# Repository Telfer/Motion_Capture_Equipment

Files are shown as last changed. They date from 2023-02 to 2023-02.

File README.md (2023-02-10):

# Motion_Capture_Equipment
 Just some bits and bobs that were developed while working in and around motion capture labs for the past few years

## Marker skeleton

Mesh files: marker_holder.stl

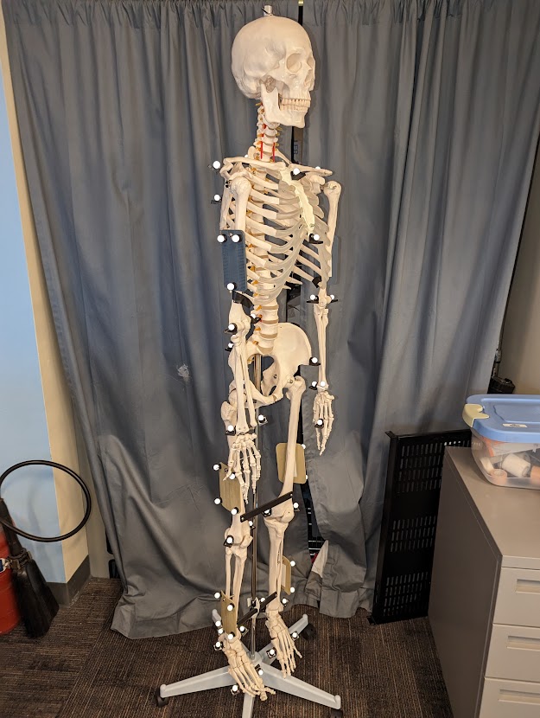
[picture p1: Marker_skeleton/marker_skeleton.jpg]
Marker skeleton


After forgeting to put a marker on for the n-th time, I bought a cheap anatomical skeleton, printed these little marker holders, and started using this set up as a way both to store the markers (pre-taped) and show the landmarks where they need to go. We just put the skeleton next to the participant and transfer the markers over one at a time. Usually easy to see if one has been missed. If you use multiple marker sets you could potentially color code or something. 

Designed for ~18mm (3/4 inch) tape. I used short (~12mm) M3 or M4 screws to attach the marker holders to the bones, along with longer ones to hang the marker plates from. Depending on your skeleton, you may also need to make extra plates to attach between bones and stop it swinging around.

## Marker plates

Mesh files: marker_plate_120-72-11.stl, marker_plate_120-80-9.stl, and marker_plate_120-60-6.stl

These do the job and are a lot less expensive than the ones I've seen commericially. The stl files are the plates I use for shank, thigh, and upper arm. These seem to work well but can be easily scaled to generate custom sizes. Be sure to print flat on the build plate for optimal strength. Both PETG and PLA have worked for me. I just superglue markers to each corner.

## Hindfoot wand

Mesh files: HeelPlate.stl, MarkerPlate.stl

Two-part marker plate designed to allow a shoe with a heel window cut in it to be taken on and off during a motion capture study (for example on different types of foot orthoses). Instructions on use in the pdf. Used in [Dose response effects of FOs](https://pubmed.ncbi.nlm.nih.gov/23631857/) and a few other papers.

## Markers with radio-opaque centers

Mesh files: Marker_RO_center_bottom.stl, Marker_RO_center_top.stl

We use these for biplane fluoroscopy studies that also require optical motion capture measurements. The marker is printed in 2 parts, a steel ball bearing is placed in the center and the 2 halves glued together. Finally, cover the marker in reflective 3M tape and you have a marker that can be measured using both biplane and standard motion capture systems. I've included stl files for a sample 9mm marker with for 3mm diameter center bead (we use these for feet), but there is also a quick python script for Rhino to generate custom markers with different hole and overall sizes.

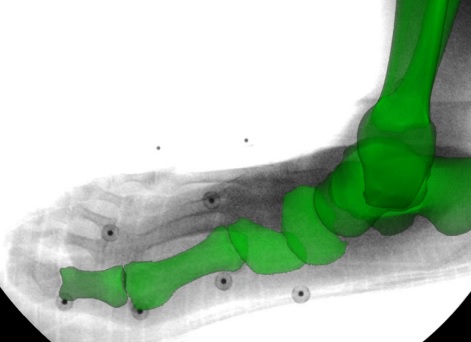
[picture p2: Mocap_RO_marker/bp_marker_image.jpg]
Marker under fluoroscopy


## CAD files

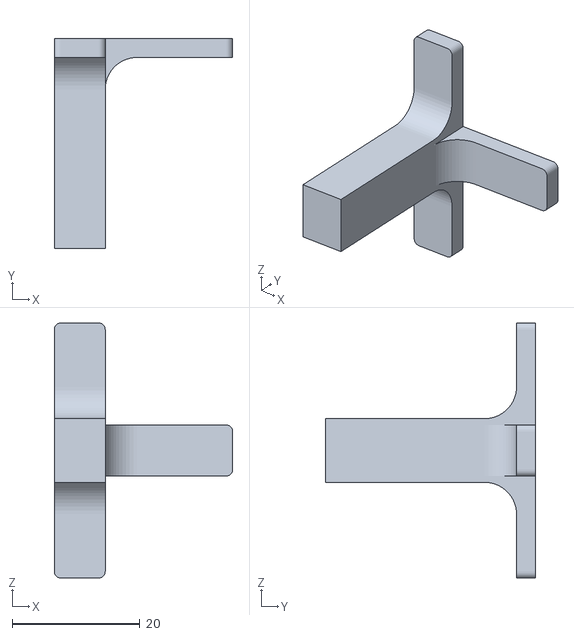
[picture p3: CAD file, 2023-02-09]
Hindfoot_wand/MarkerPlate.stl
28.0 x 33.0 x 40.0

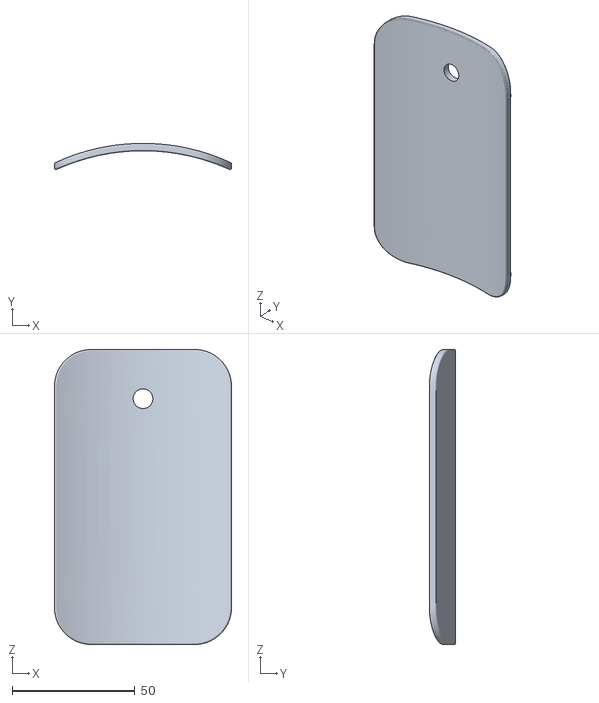
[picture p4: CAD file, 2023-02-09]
Marker_plates/marker_plate_120-72-11.stl
72.0 x 10.7 x 120.0

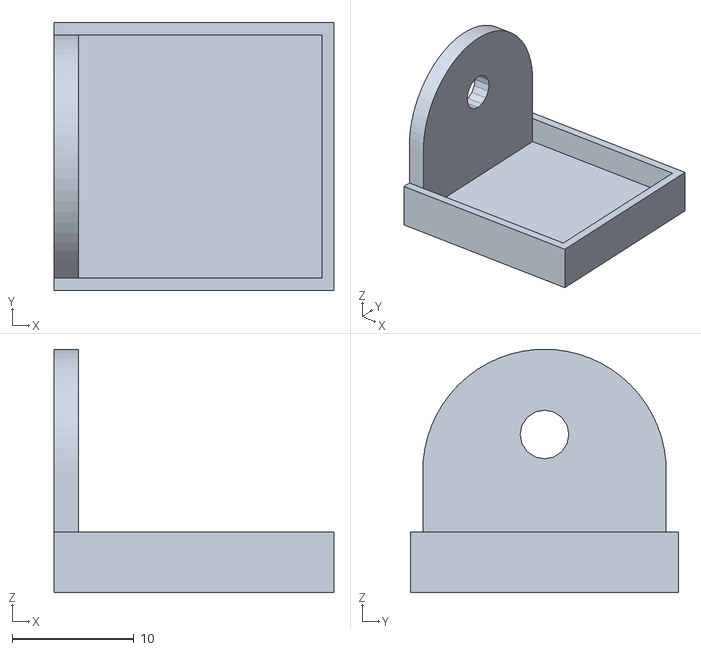
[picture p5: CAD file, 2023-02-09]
Marker_skeleton/marker_holder.stl
23.0 x 22.0 x 20.0

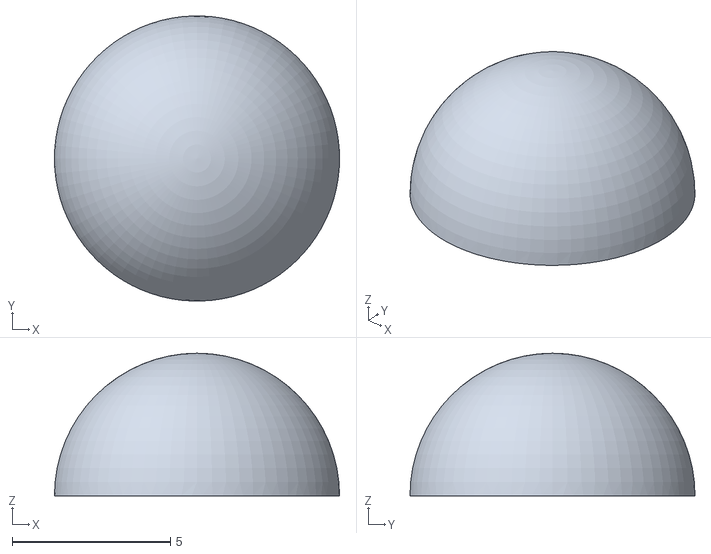
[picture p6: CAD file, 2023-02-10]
Mocap_RO_marker/Marker_RO_center_top.stl
9.00 x 8.99 x 4.50

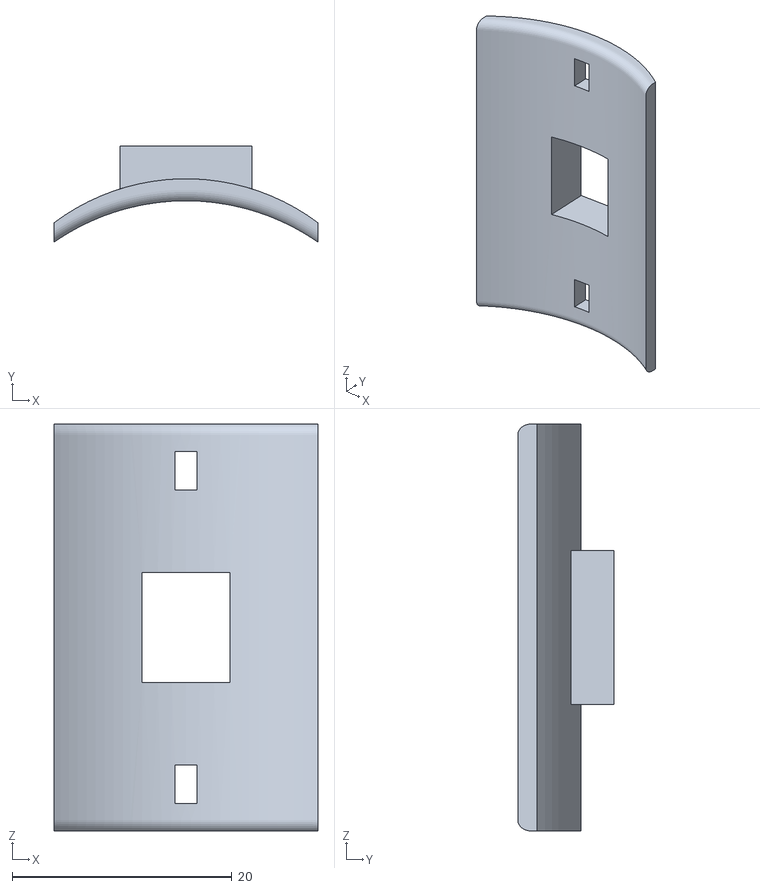
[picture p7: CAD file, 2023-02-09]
Hindfoot_wand/HeelPlate.stl
24.0 x 8.77 x 37.0

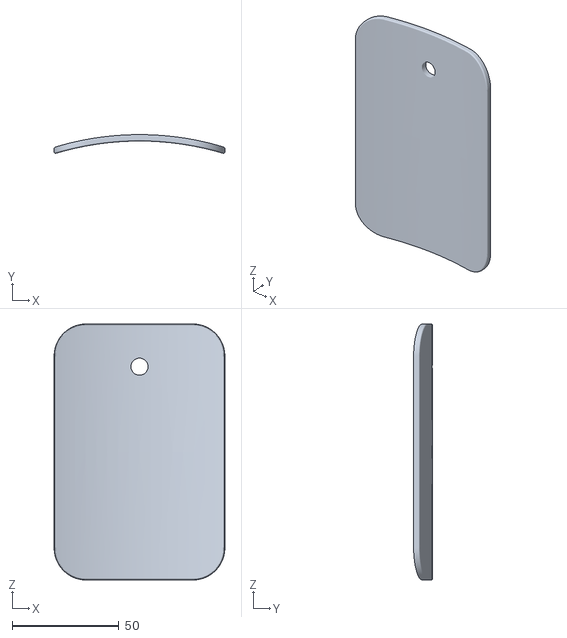
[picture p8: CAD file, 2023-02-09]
Marker_plates/marker_plate_120-80-9.stl
80.0 x 8.79 x 120.0

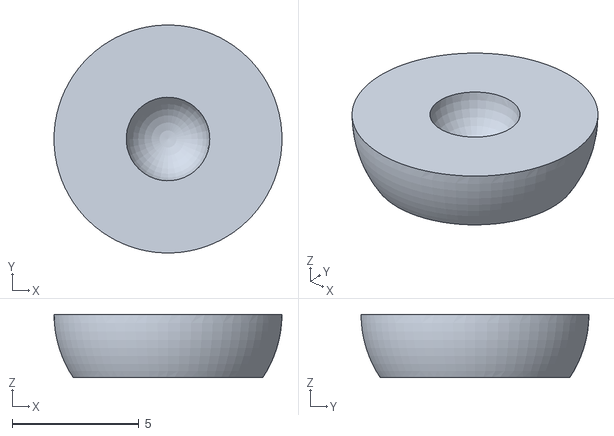
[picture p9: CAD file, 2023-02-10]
Mocap_RO_marker/Marker_RO_center_bottom.stl
9.00 x 8.99 x 2.50

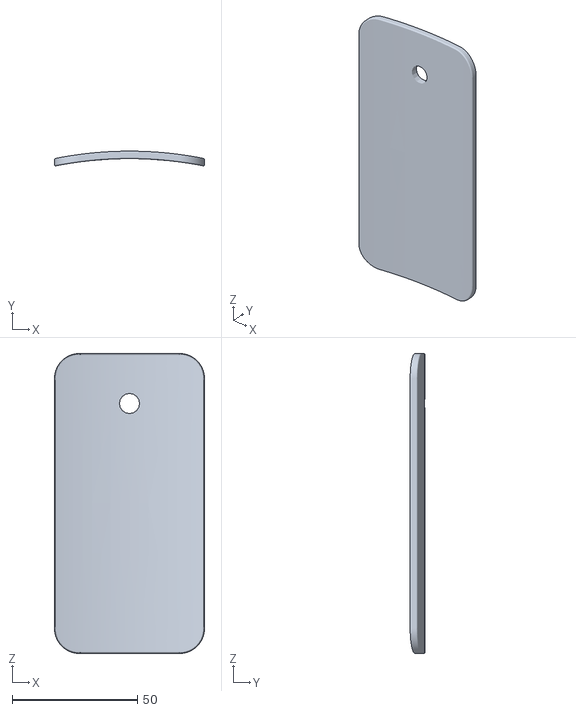
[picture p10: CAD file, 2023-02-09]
Marker_plates/marker_plate_120-60-6.stl
60.0 x 5.89 x 120.0

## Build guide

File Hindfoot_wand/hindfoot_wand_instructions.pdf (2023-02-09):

2

## Dose-response effects of customised foot orthoses on lower limb kinematics and kinetics in pronated foot type: supplementary materials

Telfer S*, Abbott M, Steultjens M, Woodburn J

All authors: School of Health and Life Sciences, Glasgow Caledonian University, UK

*Corresponding author

Address: Institute of Applied Health Research, Glasgow Caledonian University, Cowcaddens Road, Glasgow, UK, G4 0BA

Telephone: +44 (0) 141 331 8475

Email: scott.telfer@gcu.ac.uk

3

## Contents

4

## 1. Motion capture model

### 1.1 Marker locations

All retroreflective motion capture markers were flat-based spherical type (Qualysis AB, Gothenburg, Sweden). Marker locations and details are described in Table S1 and Figure S1.

Table S1 –Marker locations, labels and function
Number | Landmark/Location | Label Name | Size (mm) | Remove*/Track
1 | Right anterior iliac spine | RAIS | 19 | Tracking
2 | Right greater trochanter | RGT | 19 | Remove
3 | Right posterior iliac spine | RPIS | 19 | Tracking
4 | Left anterior iliac spine | LAIS | 19 | Tracking
5 | Left greater trochanter | LGT | 19 | Remove
6 | Left posterior iliac spine | LPIS | 19 | Tracking
7 | Thigh 1st | THI1 | 19 | Tracking
8 | Thigh 2nd | THI2 | 19 | Tracking
9 | Thigh 3rd | THI3 | 19 | Tracking
10 | Thigh 4th | THI4 | 19 | Tracking
11 | Lateral epicondile | LKNE | 12 | Remove
12 | Medial epicondile | MKNE | 12 | Remove
13 | Shin 1st | SHN1 | 19 | Tracking
14 | Shin 2nd | SHN2 | 19 | Tracking
15 | Shin 3rd | SHN3 | 19 | Tracking
16 | Shin 4th | SHN4 | 19 | Tracking
17 | Medial malleolus | MMAL | 7 | Remove
18 | Lateral malleolus | LMAL | 7 | Remove
19 | Superior calcaneum | SCAL | 7 | Tracking
20 | Inferior calcaneum | ICAL | 7 | Tracking
21 | Lateral offset calcaneum | OCAL | 7 | Tracking
22 | Medial calcaneum | MCAL | 7 | Remove
23 | Tuberosity navicular | NAV | 12 | Tracking
24 | Proximal 1st met | P1MT | 7 | Remove
25 | Medial 1st met head | M1MH | 12 | Tracking
26 2
| nd Met Head | D2MT | 7 | Remove
27 | Lateral calcaneum | LCAL | 7 | Remove
28 | Proximal 5th met | P5TH | 12 | Tracking
29 | Distal 5th met | D5TH | 12 | Tracking
*Remove: Required for model building only, removed after static trial has been captured

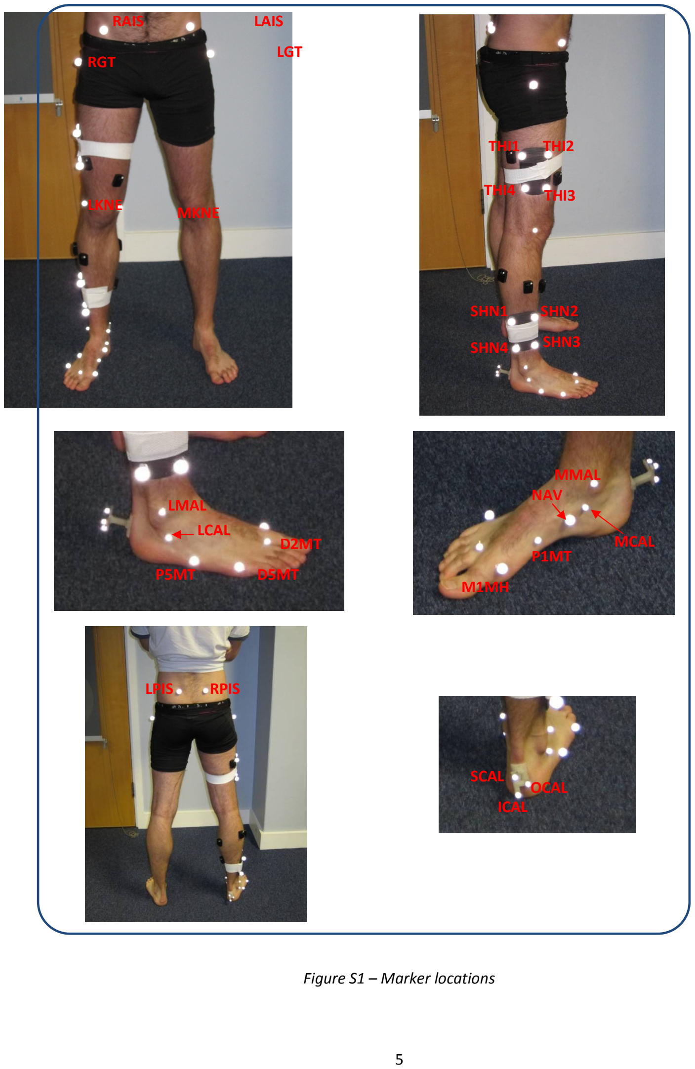
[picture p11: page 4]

5

Figure S1 – Marker locations

LGT

MKNE LKNE

RAIS | LAIS

RGT

THI1 THI2

THI3 THI4

SHN1 SHN2

SHN3 SHN4

MMAL

MCAL

NAV

P1MT

M1MH

SCAL

ICAL

OCAL

LPIS RPIS

D2MT

P5MT | D5MT

LCAL

LMAL

6

### 1.2 Anatomical reference frame definitions

Table S2 – Anatomical reference frame definitions for individual segments
Segment | Description
Pelvis | CODA¹
Thigh
Origin | Virtual HIP_CENTRE marker from CODA pelvis
z-axis | The z-axis is the projection of the line joining HIP_CENTRE and the origin.
x-axis | The x-axis is perpendicular to the z-axis in a plane containing the origin, KNEE, and LKNEE.
y-axis | The y-axis is mutually perpendicular to the x- and z-axes
Shank
Origin | A virtual KNEE marker was created 50% of the distance on the line between the LKNEE and MKNEE
| markers.
z-axis | A virtual marker, MAL_CENTRE is created 50% of the distance between the MMAL and LMAL markers.
| The z-axis is the projection of the line joining MAL_CENTRE and the origin.
x-axis | The x-axis is perpendicular to the z-axis in a plane containing the origin, MAL-centre and LMAL.
y-axis | The y-axis is mutually perpendicular to the x- and z-axes.
Rearfoot
Origin | A virtual marker is projected perpendicularly from SCAL onto a plane created by ICAL and virtual
| markers projected from ICAL in X + and Z + a nominal distance of 0.1m. The rearfoot origin is located
| here.
z-axis | The z-axis is the projection of the line joining ICAL and the rearfoot origin.
x-axis | The x-axis is perpendicular to the z axis in a plane containing the origin, ICAL and HF_X. HF_X is a
| virtual marker projected from the origin in the X + , a nominal distance of 0.1m.
y-axis | The y-axis is mutually perpendicular to the x- and z-axes.
Forefoot
Origin | Virtual markers are projected from P1MT (P1MT_PROJ) and P5MT (P5MT_PROJ) perpendicularly onto
| a plane created by D5MT and virtual markers projected from D5MT in X + and Y⁺ a nominal distance
| of 0.1m. The origin of the forefoot is then located at the midpoint (50% distance) between
| P1MT_PROJ and P5MT_PROJ.
y-axis | A virtual D2MT marker (D2MT_PROJ) is projected perpendicularly onto a plane created by D5MT and
| virtual markers projected from D5MT in X + and Y⁺ a nominal distance of 0.1m. The y-axis is a
| projection of the line joining the origin to D2MT_PROJ.
x-axis | The x-axis is perpendicular to the y-axis in a plane containing the origin, D2MT_PROJ and D5MT.
z-axis | The z-axis is mutually perpendicular to the y- and x-axes.
Foot
Origin | The origin is located at the virtual MAL_CENTRE marker.
y-axis | Virtual markers are created from projections in Y + from M1MH (M1MH_PROJ) and D5MT (D5MT_PROJ)
| to the longest toe. These distances are derived from calliper measurements for each subject. The y-
| axis is a projection of the line joining the origin and a virtual marker (DISTAL_FOOT_CENTRE) 50%
| distance between M1MH_PROJ and D5MT_PROJ.
z-axis | The z-axis is perpendicular to the y-axis in a plane containing the origin, DISTAL_FOOT_CENTRE and
| shank origin.
x-axis | The x-axis is mutually perpendicular to the y- and z-axes.

1

See http://www.c-motion.com/v3dwiki/index.php?title=Coda_Pelvis (last accessed 9th October 2012).

7

The landmarks outlined in Table S1, along with projected or virtual markers created within the Visual3D software system were used to define the segment anatomical reference frames (see Table S2). Orientation of the axes was standardised such that the X-axis was medial/lateral with X

+
pointing to the right; the Y-axis was anterior/posterior with Y

+
pointing forward; and the Z-axis as vertical with Z

+
pointing upwards.

### 1.3 Joint rotation definitions

The cardan sequence order of rotation was x-y-z. Intersegment rotations were defined using clinical meaningful terms. For the reported results, the knee joint kinetics were expressed in the local coordinate system of the thigh. Therefore external adduction (+) / abduction (-) moments occurred about the y-axis. Ankle joint kinetics were expressed in the local coordinate system of the shank. Therefore inversion (+) / eversion (-) occurred about the y-axis.

Rearfoot motion was expressed in the local coordinate system of the shank. Therefore inversion (+) / eversion (-) occurred about the y-axis. Motion of the tibia was expressed in the local coordinate system of the rearfoot. Therefore external (+) / internal (-) rotation was expressed about the z-axis. Forefoot motion was expressed in the local coordinate system of the rearfoot. Therefore adduction (+) / abduction (-) rotation occurred about the z-axis.

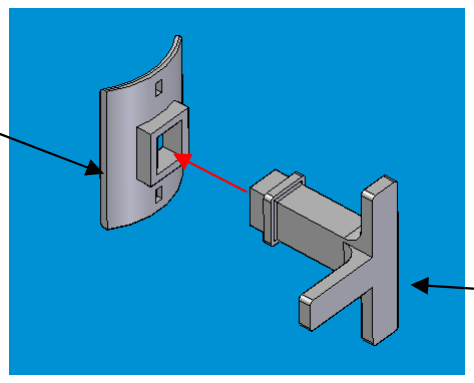
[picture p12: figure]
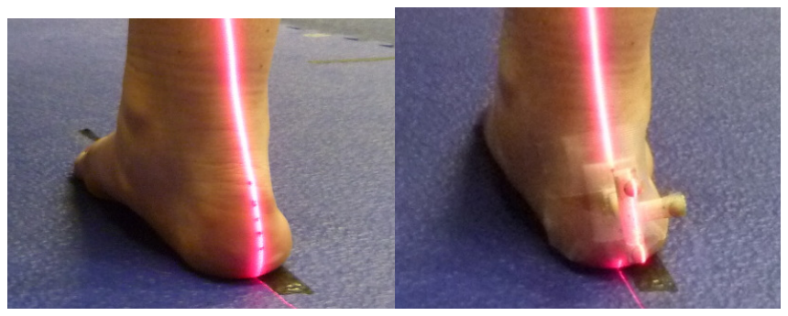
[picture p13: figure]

8

## 2. Footwear and accessories

### 2.1 Rearfoot wand

The rearfoot wand (Figure S2) is in two sections to allow a shoe to be donned and doffed without the need to fully remove and replace the wand, a process which would introduce error into the measurement. The wand is made up of a “plate” part, which is stuck to the participant’s heel, and the removable “wand” section which slots into a hole in the plate and has three markers stuck to it (SCAL, ICAL and OCAL). All parts were made in polyacidite via a fused deposition 3D printing method. The rearfoot wand and its CAD models are available on request from the corresponding author (scott.telfer@gcu.ac.uk).

Figure S2 – Detachable rearfoot wand

### 2.2 Positioning of rearfoot wand

Figure S3 – Alignment of rearfoot wand

To ensure accurate alignment of the rearfoot wand with the rearfoot in the frontal plane, the following protocol was used-

1. The calcaneal bisection line is drawn on the participant’s heel using a dark coloured nonpermanent marker.
2. The foot is positioned on the floor such that the 2nd toe and centre of the heel are aligned against a straight line marked on the floor while the participant stands in a relaxed position.
3. A line laser (red line laser, adjustable focus; A1 Technologies, London, UK) is positioned such that, when its line is vertical, it is aligned with the previously described line on the

WAND

PLATE

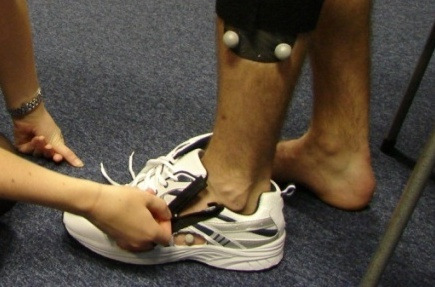
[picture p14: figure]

9

floor (see Figure S3). The laser is used to project a line onto the heel and lower leg. This laser is rotated until the projected line passes through the calcaneal bisection line previously marked on the heel (i.e. it matches the relaxed calcaneal stance position angle).

4. The rearfoot wand is then positioned so that laser line passes through the middle of both SCAL and ICAL markers (see figure S3).

### 2.3 Adapted shoe

A specially adapted neutrally posted training shoe was used in this study. The shoe has holes cut to allow the M1MH, P1MT, NAV and D5MT markers to be viewed as well as a hole in the heel counter to allow the rearfoot wand to stick through. Zips are sewn into the medial and lateral sides of the shoe to allow the upper to be opened up and the foot removed from the shoe without the need to remove and replace markers, while maintaining the structural integrity of the shoe.

As shown in Figure S4, to change the orthotic being worn, the detachable wand section of the rearfoot wand is carefully removed from the plate (leaving the plate attached to the foot) and the zips on the lateral and medial sides of the shoe are undone. The upper section opened out, and the researcher holds out the sides of the shoe. The participant is asked to push their toes as far as possible to the front of the shoe, then to first lift their heel out followed by the rest of the foot. This process is reversed to don the shoe.

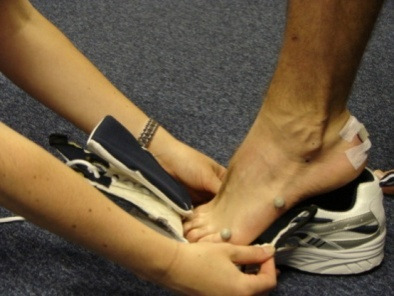
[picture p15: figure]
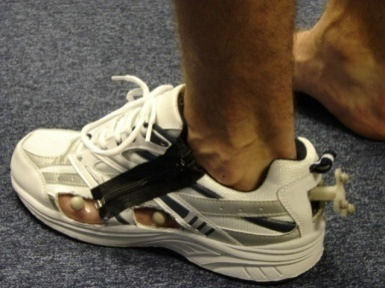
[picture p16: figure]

Figure S4 – Adapted shoe and process for changing orthotic

## 3. Additional results

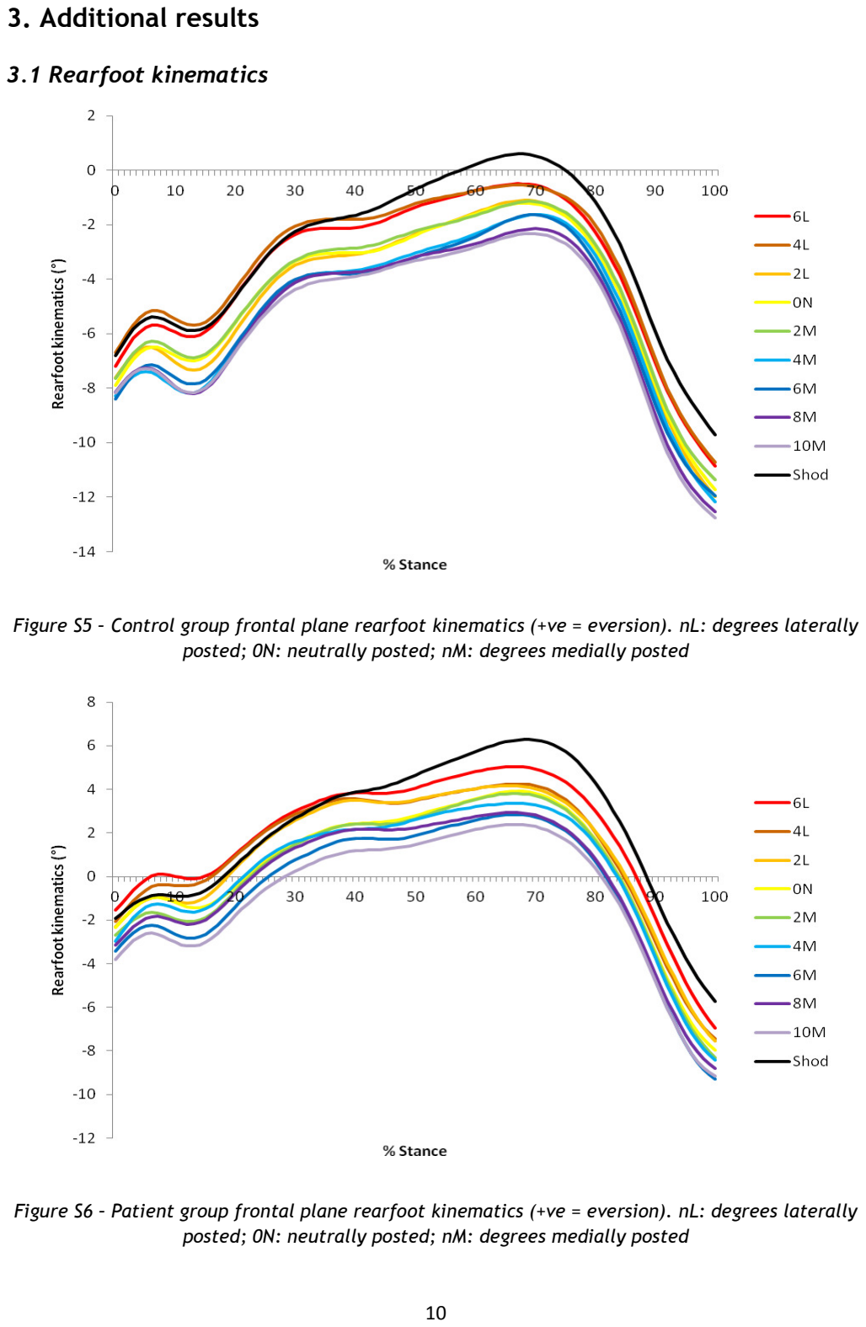
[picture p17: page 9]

10

### 3.1 Rearfoot kinematics

Figure S5 – Control group frontal plane rearfoot kinematics (+ve = eversion). nL: degrees laterally posted; 0N: neutrally posted; nM: degrees medially posted

Figure S6 – Patient group frontal plane rearfoot kinematics (+ve = eversion). nL: degrees laterally posted; 0N: neutrally posted; nM: degrees medially posted

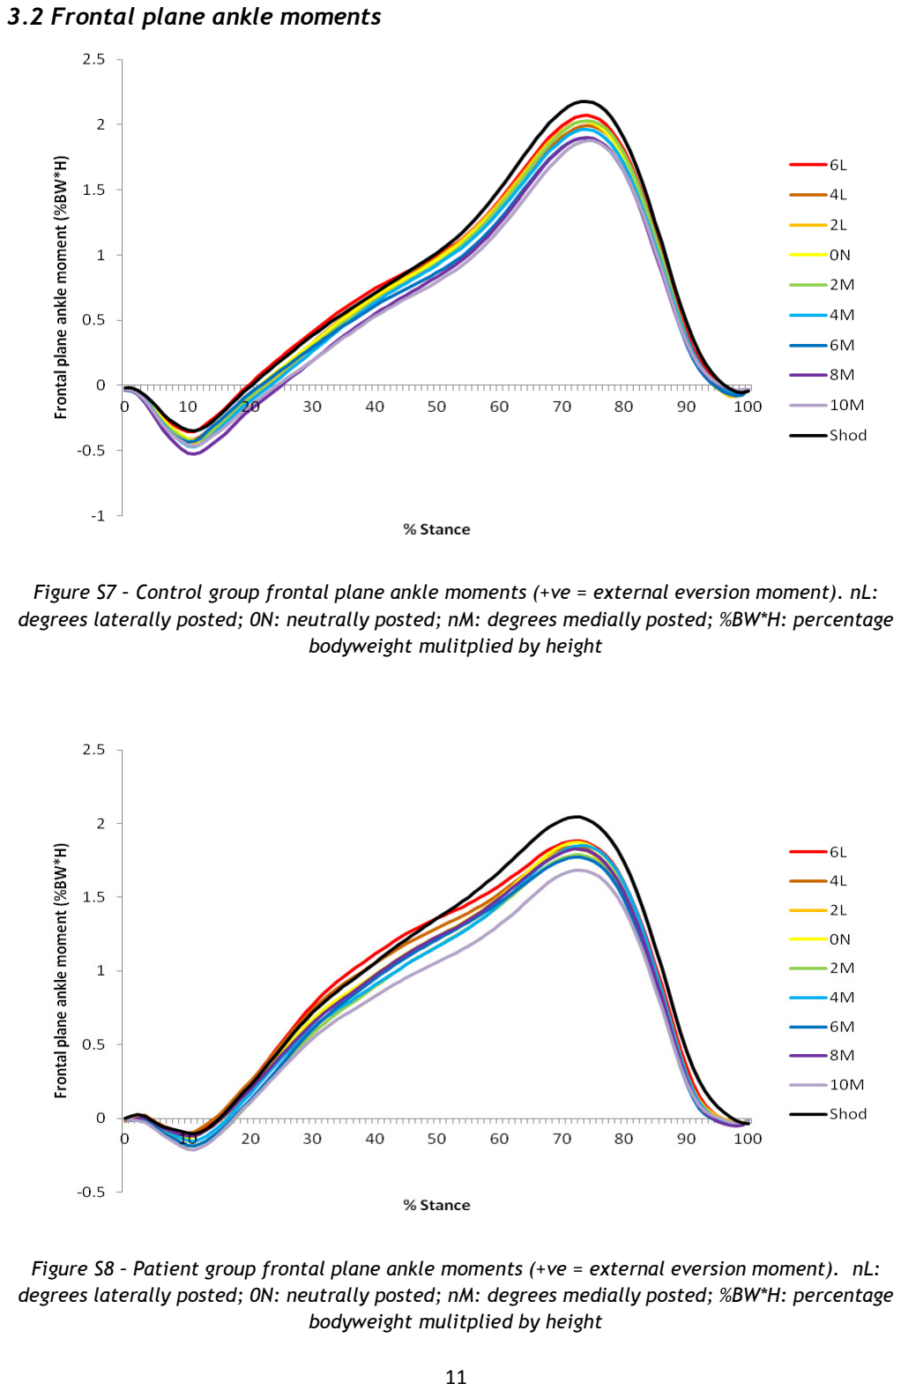
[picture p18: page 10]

11

### 3.2 Frontal plane ankle moments

Figure S7 – Control group frontal plane ankle moments (+ve = external eversion moment). nL: degrees laterally posted; 0N: neutrally posted; nM: degrees medially posted; %BW*H: percentage bodyweight mulitplied by height

Figure S8 – Patient group frontal plane ankle moments (+ve = external eversion moment). nL: degrees laterally posted; 0N: neutrally posted; nM: degrees medially posted; %BW*H: percentage bodyweight mulitplied by height

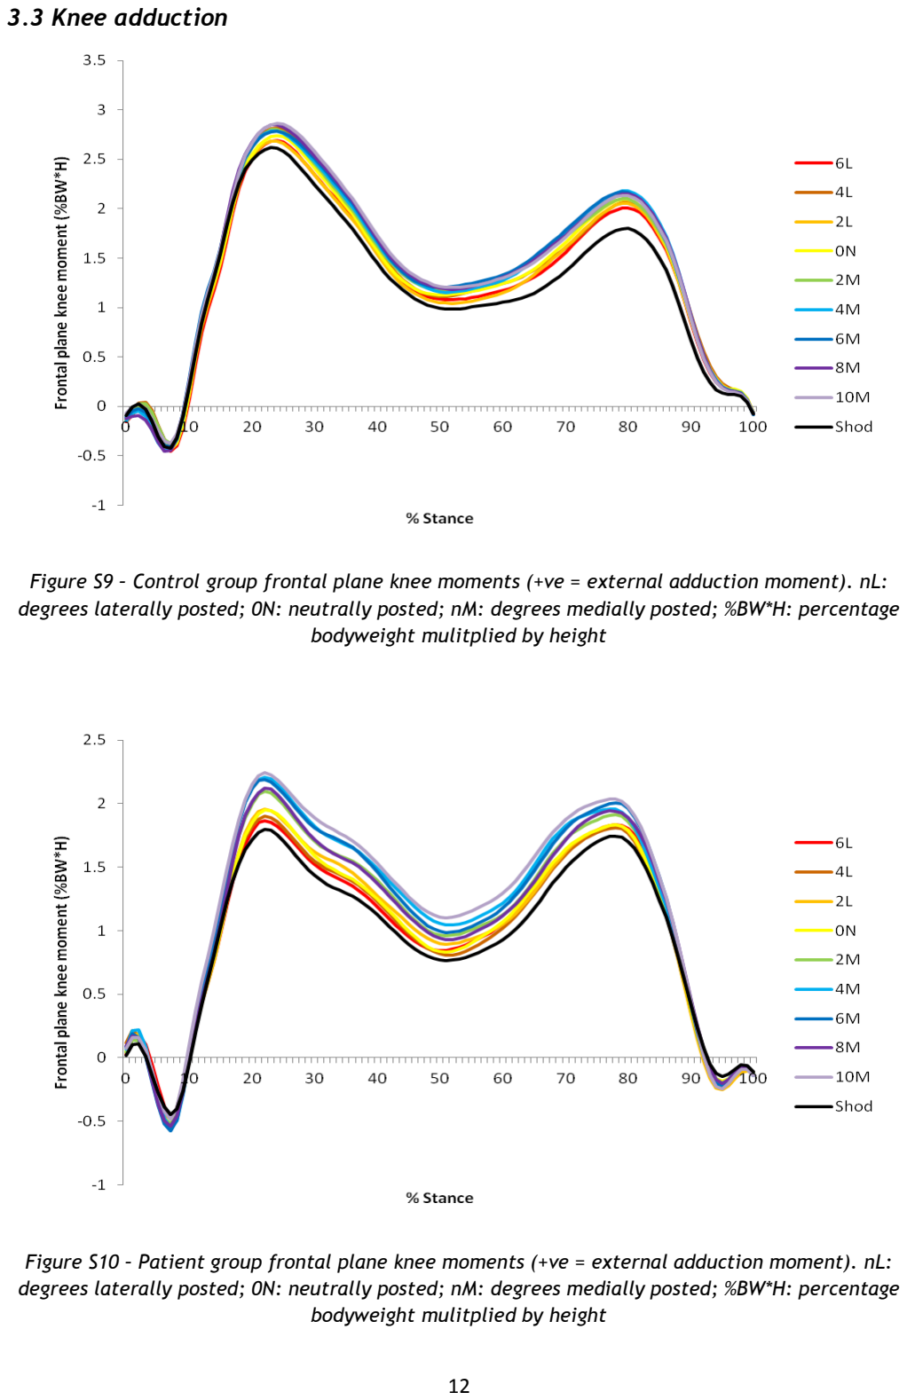
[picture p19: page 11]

12

### 3.3 Knee adduction

Figure S9 – Control group frontal plane knee moments (+ve = external adduction moment). nL: degrees laterally posted; 0N: neutrally posted; nM: degrees medially posted; %BW*H: percentage bodyweight mulitplied by height

Figure S10 – Patient group frontal plane knee moments (+ve = external adduction moment). nL: degrees laterally posted; 0N: neutrally posted; nM: degrees medially posted; %BW*H: percentage bodyweight mulitplied by height

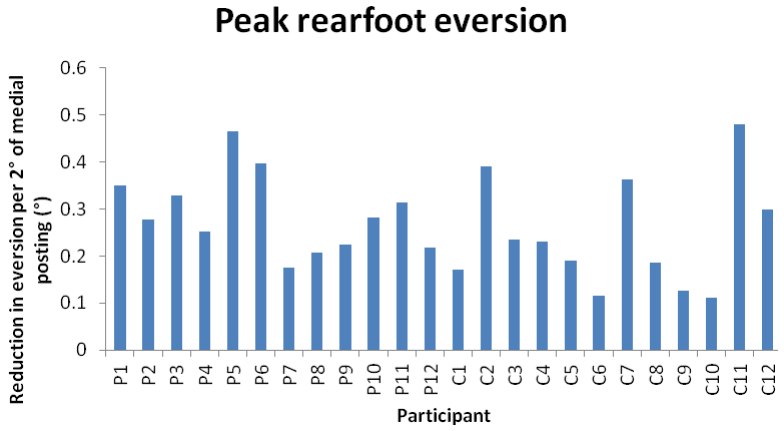
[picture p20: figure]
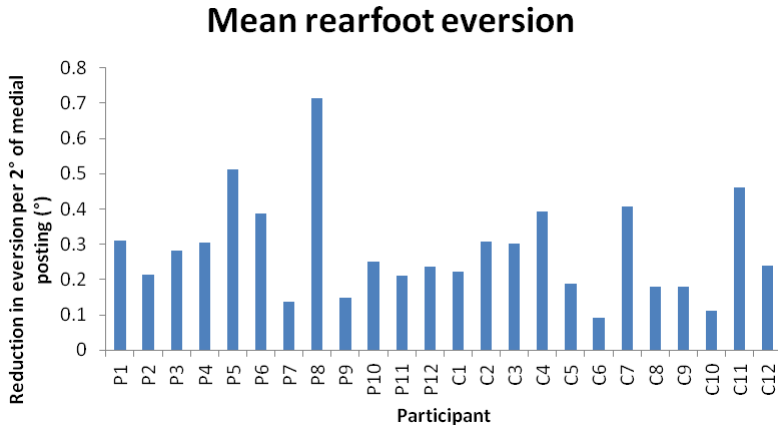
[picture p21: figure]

13

### 3.4 Individual responses

Figure S11 – Individual responses for peak rearfoot eversion. P: patient group; C: control group

Figure S12 – Individual responses for mean rearfoot eversion. P: patient group; C: control group

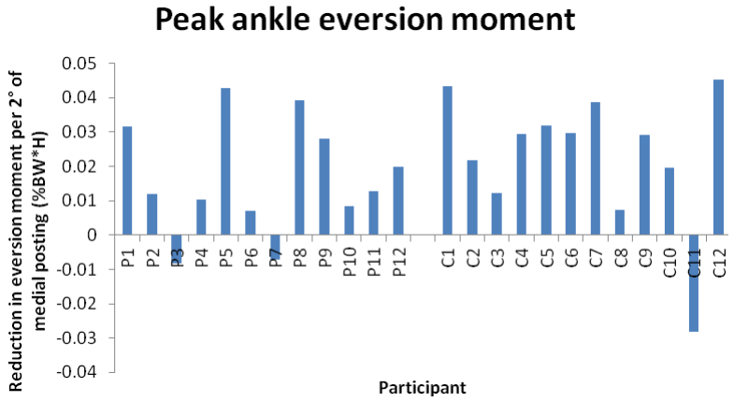
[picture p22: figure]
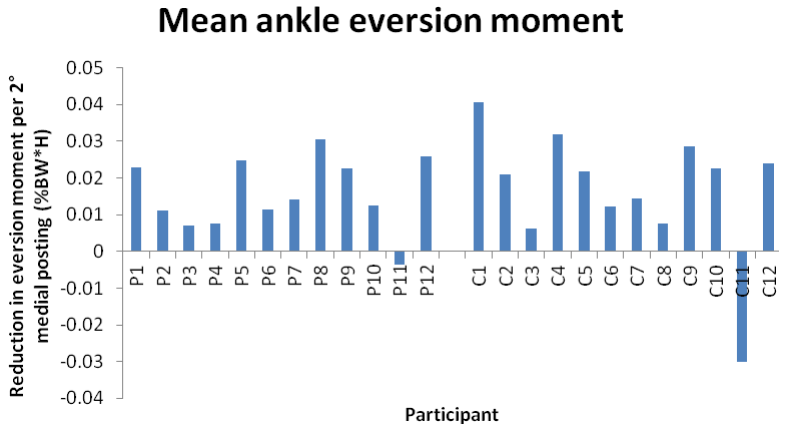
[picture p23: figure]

14

Figure S13 – Individual responses for peak external ankle eversion moment. P: patient group; C: control group; %BW*H: percentage bodyweight multiplied by height

Figure S14 – Individual responses for mean external ankle eversion moment. P: patient group; C: control group; %BW*H: percentage bodyweight multiplied by height

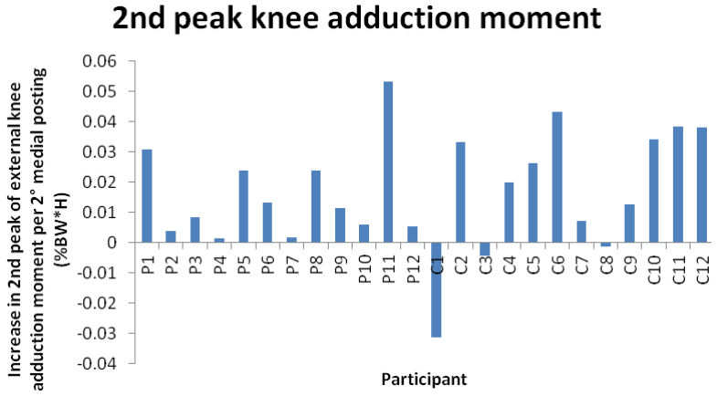
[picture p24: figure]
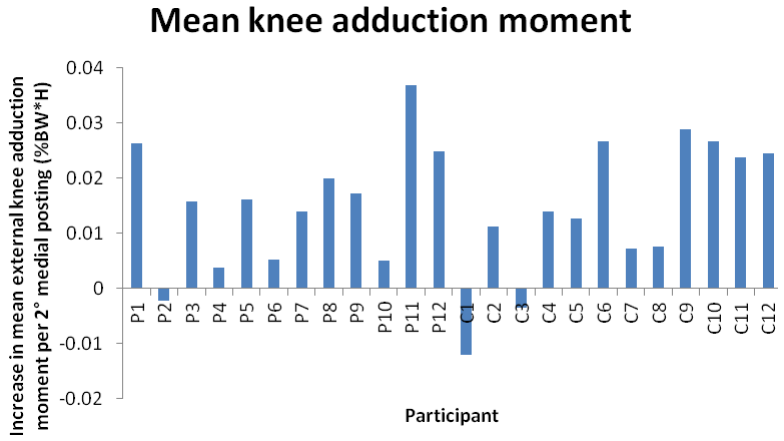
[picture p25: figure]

15

Figure S15 – Individual responses for 2nd peak external knee eversion moment. P: patient group; C: control group; %BW*H: percentage bodyweight multiplied by height.

Figure S16 – Individual responses for mean external ankle eversion moment. P: patient group; C: control group; %BW*H: percentage bodyweight multiplied by height

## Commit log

2023-02-09 Updated Readme and added stl files
    [marker_holder.stl, marker_plate_120-60-6.stl, marker_plate_120-72-11.stl, marker_plate_120-80-9.stl]
2023-02-09 Added hindfoot wand
    [HeelPlate.stl, MarkerPlate.stl, marker_holder.stl, marker_plate_120-60-6.stl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]
2023-02-10 Added RO marker
    [Marker_RO_center_bottom.stl, Marker_RO_center_top.stl]
